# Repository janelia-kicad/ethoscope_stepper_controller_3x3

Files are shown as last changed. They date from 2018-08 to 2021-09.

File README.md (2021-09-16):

- [Repository Information](#org758a3eb)
  - [Description](#orgeb4be27)
- [Images](#org71172c4)
- [Schematic](#org945219d)
- [Gerbers](#org1d6248d)
- [Bill of Materials](#orgcc7b03c)
  - [PCB Parts](#orga3dccca)
  - [Supplemental Parts](#org7db11a9)
  - [Vendor Parts Lists](#orgad09c1d)
- [Supplemental Documentation](#org79a2346)
  - [Assembly Instructions](#org838f5a4)

# Repository Information

-   **Name:** ethoscope\_stepper\_controller\_3x3
-   **Version:** 1.2
-   **License:** Open-Source Hardware
-   **URL:** <https://github.com/janelia-kicad/ethoscope_stepper_controller_3x3>
-   **Author:** Peter Polidoro
-   **Email:** peter@polidoro.io

## Description

This device controls the 7 stepper motors on the fly ethoscope rig.

# Images

# Schematic

[./schematic/ethoscope\_stepper\_controller\_3x3.pdf](./schematic/ethoscope_stepper_controller_3x3.pdf)

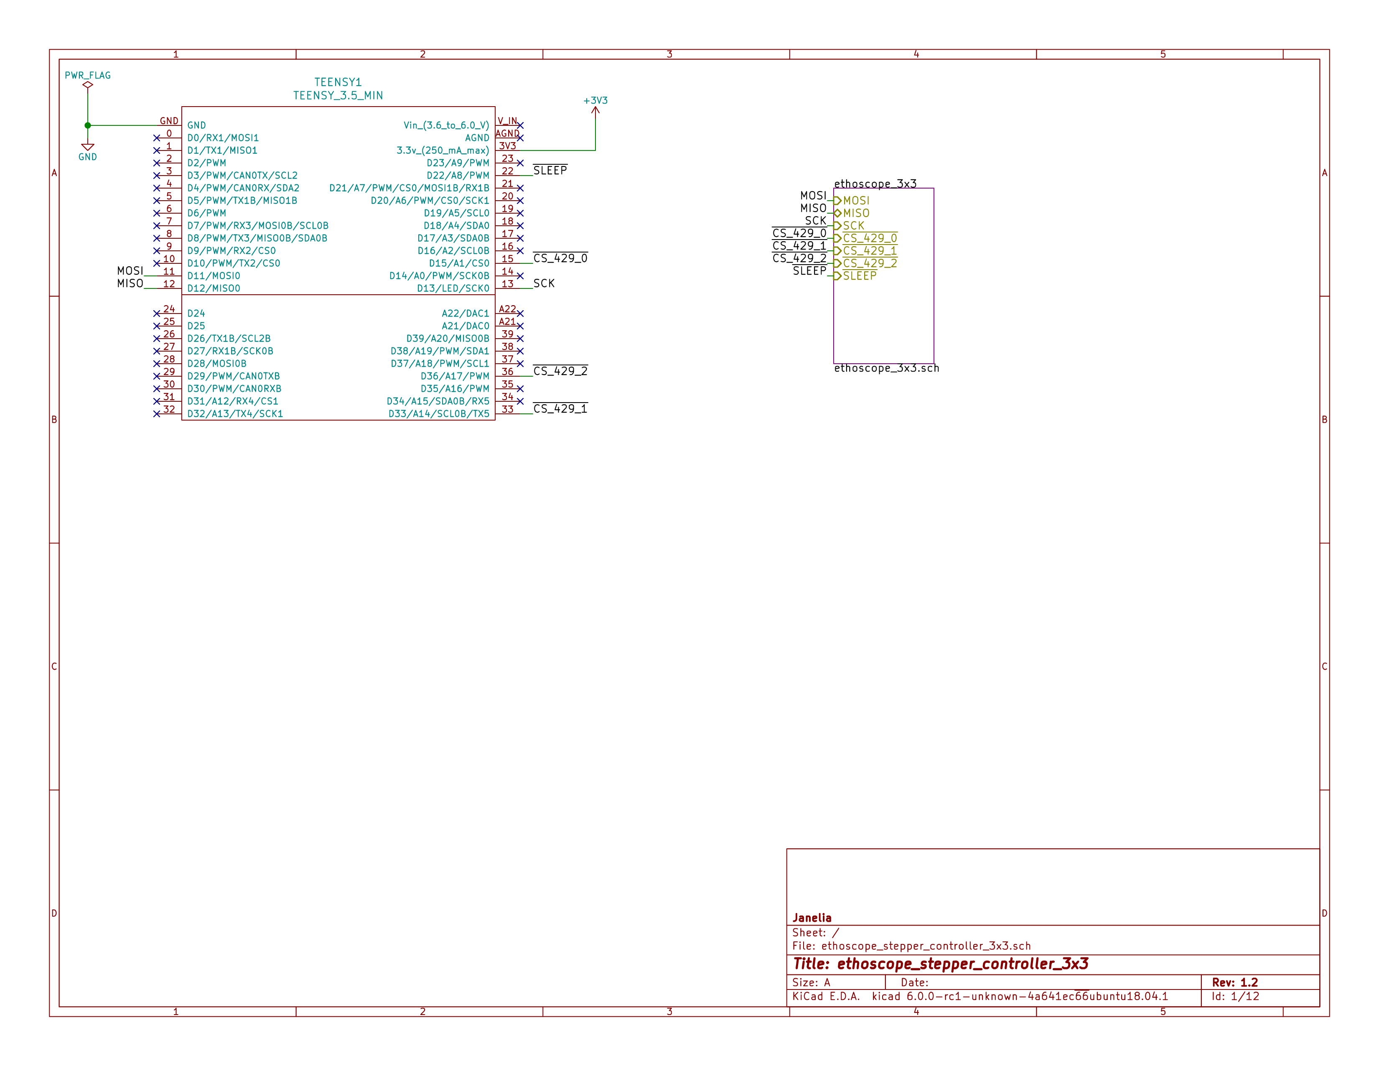
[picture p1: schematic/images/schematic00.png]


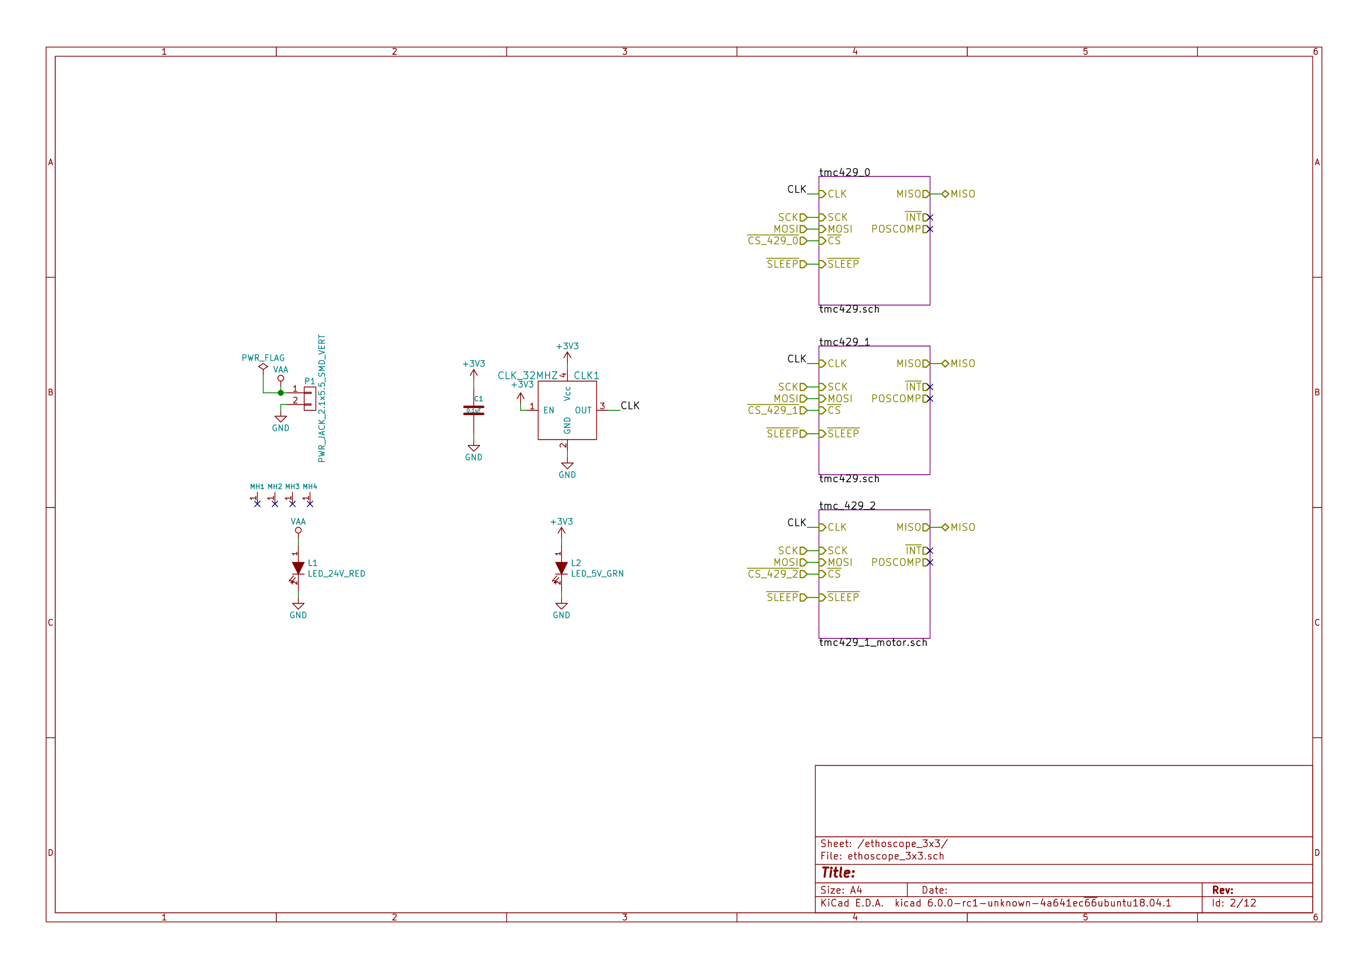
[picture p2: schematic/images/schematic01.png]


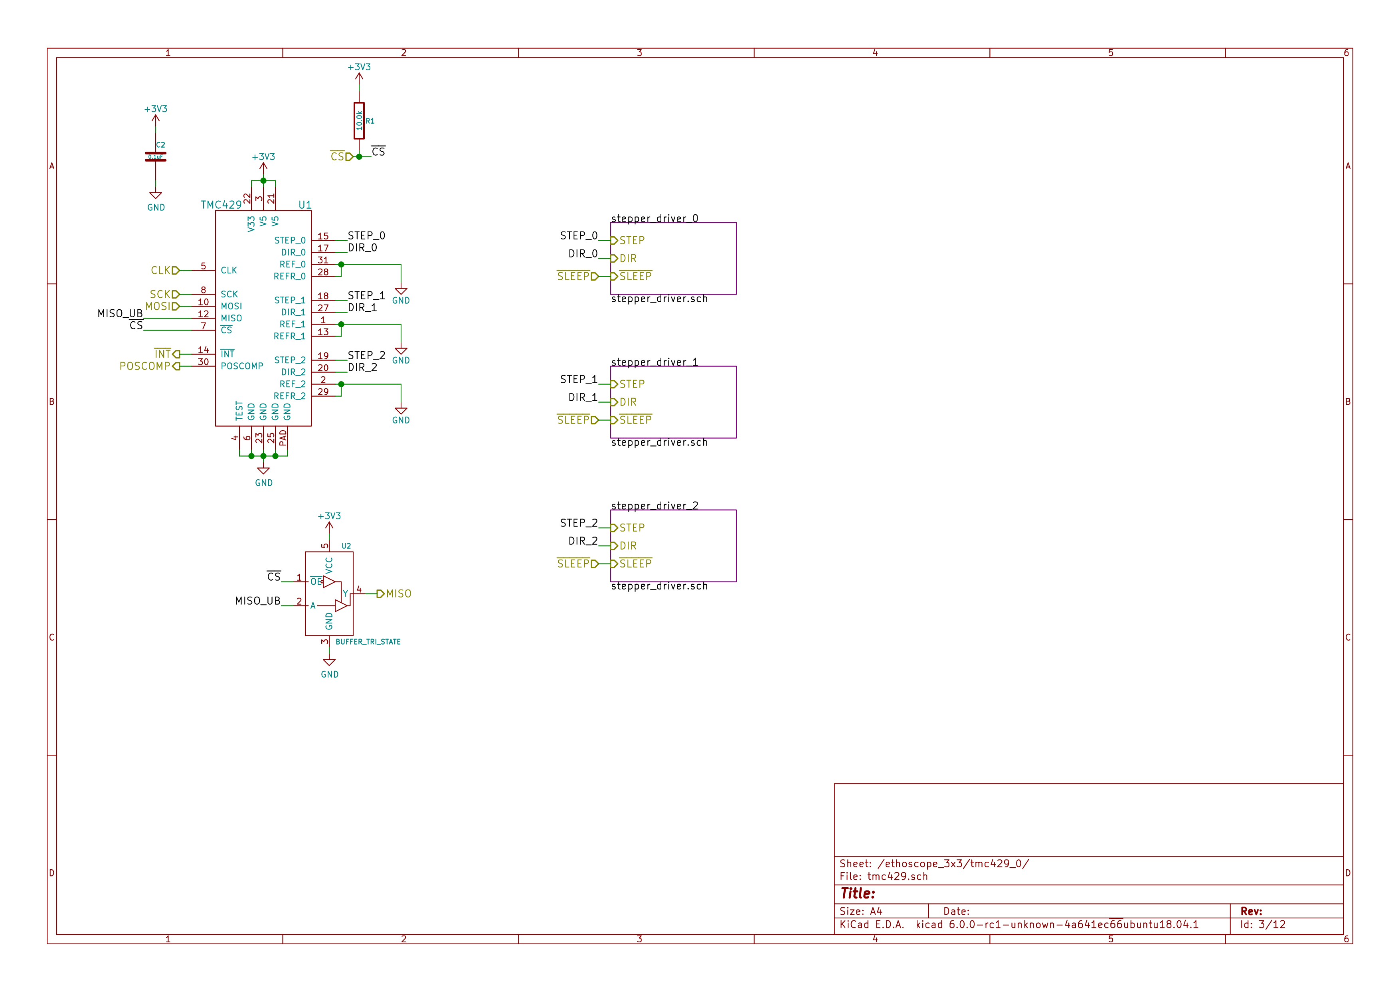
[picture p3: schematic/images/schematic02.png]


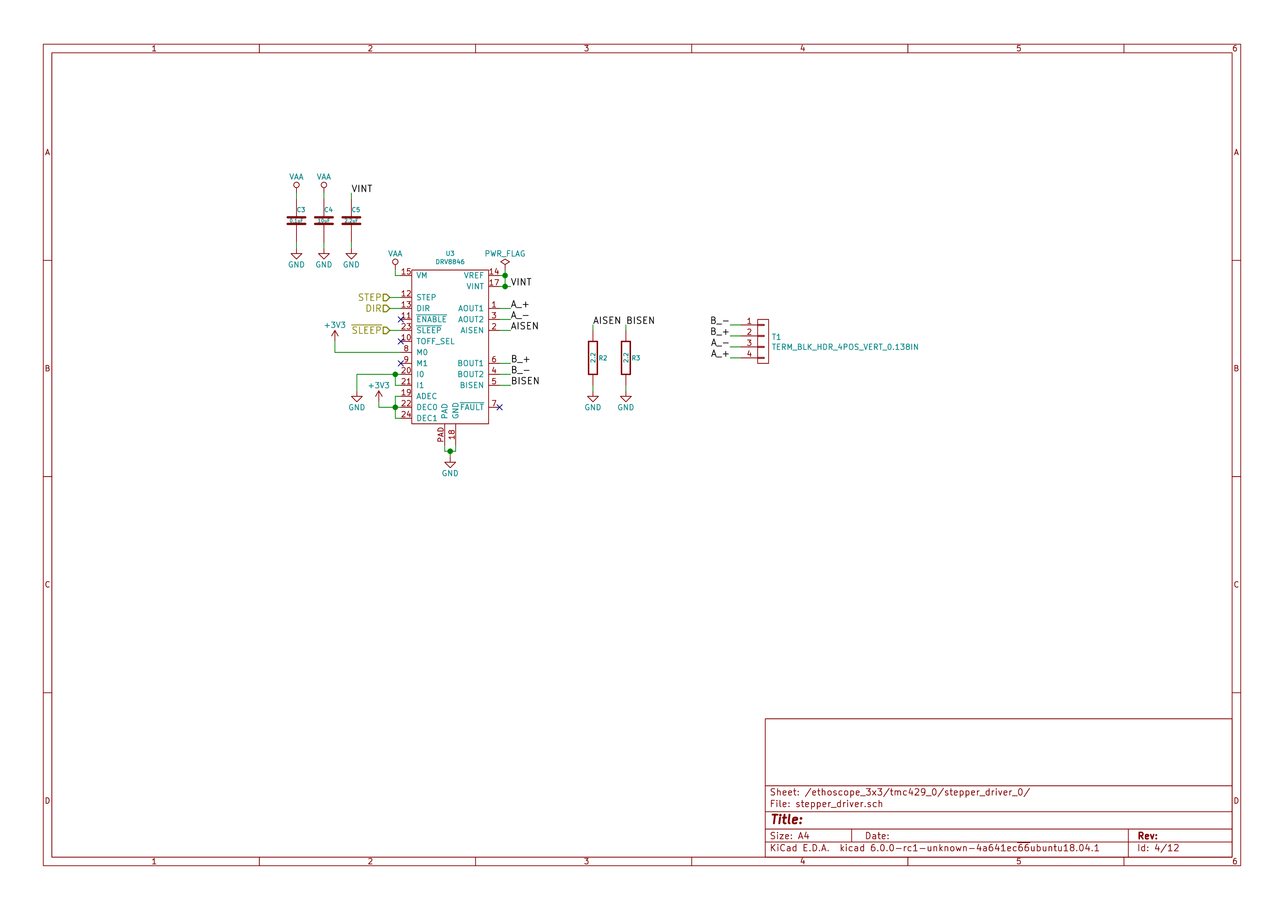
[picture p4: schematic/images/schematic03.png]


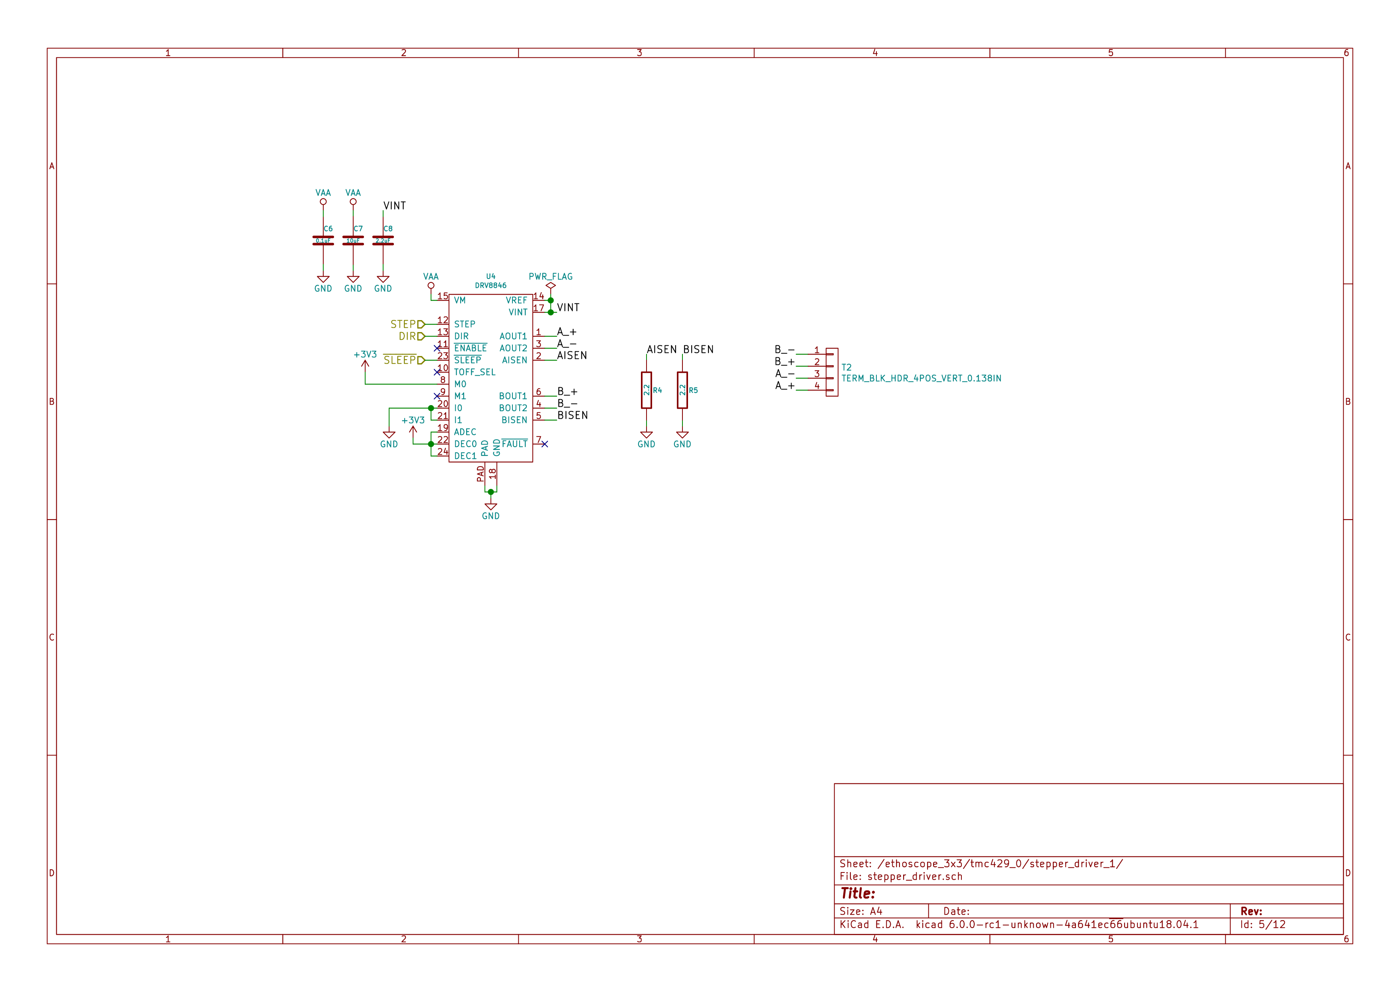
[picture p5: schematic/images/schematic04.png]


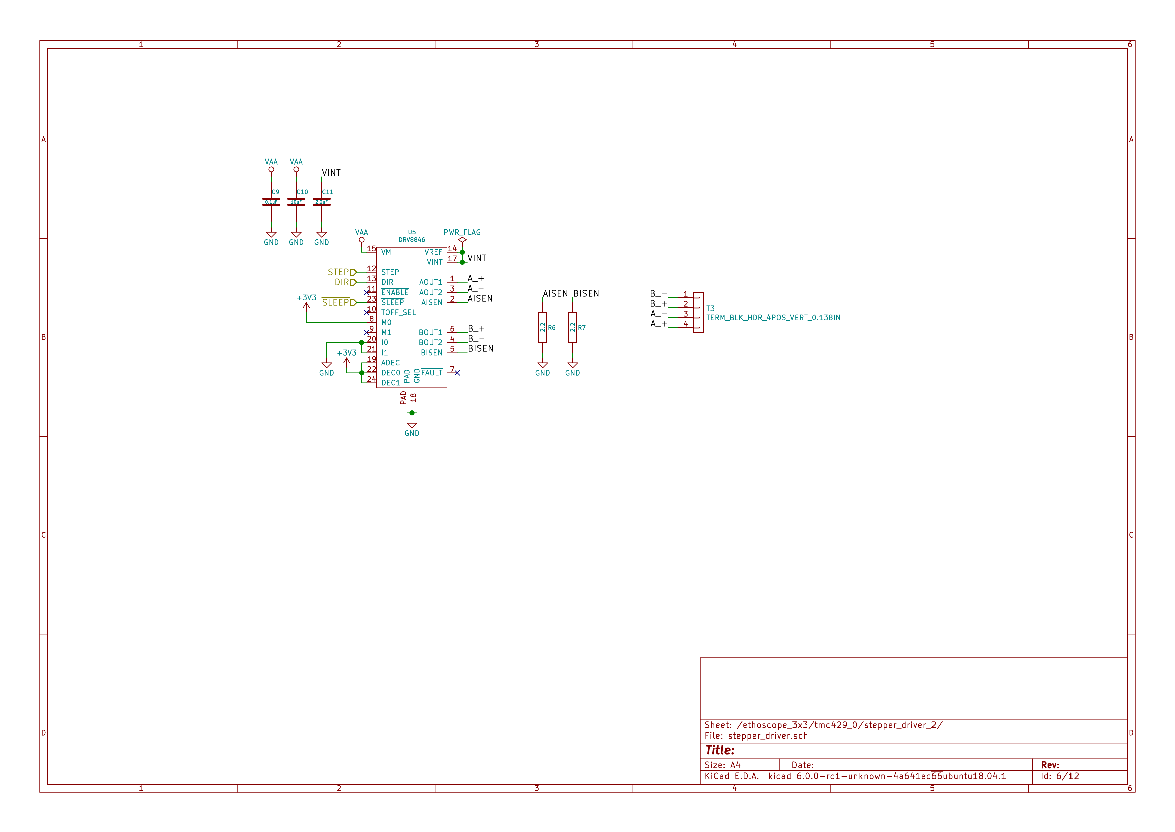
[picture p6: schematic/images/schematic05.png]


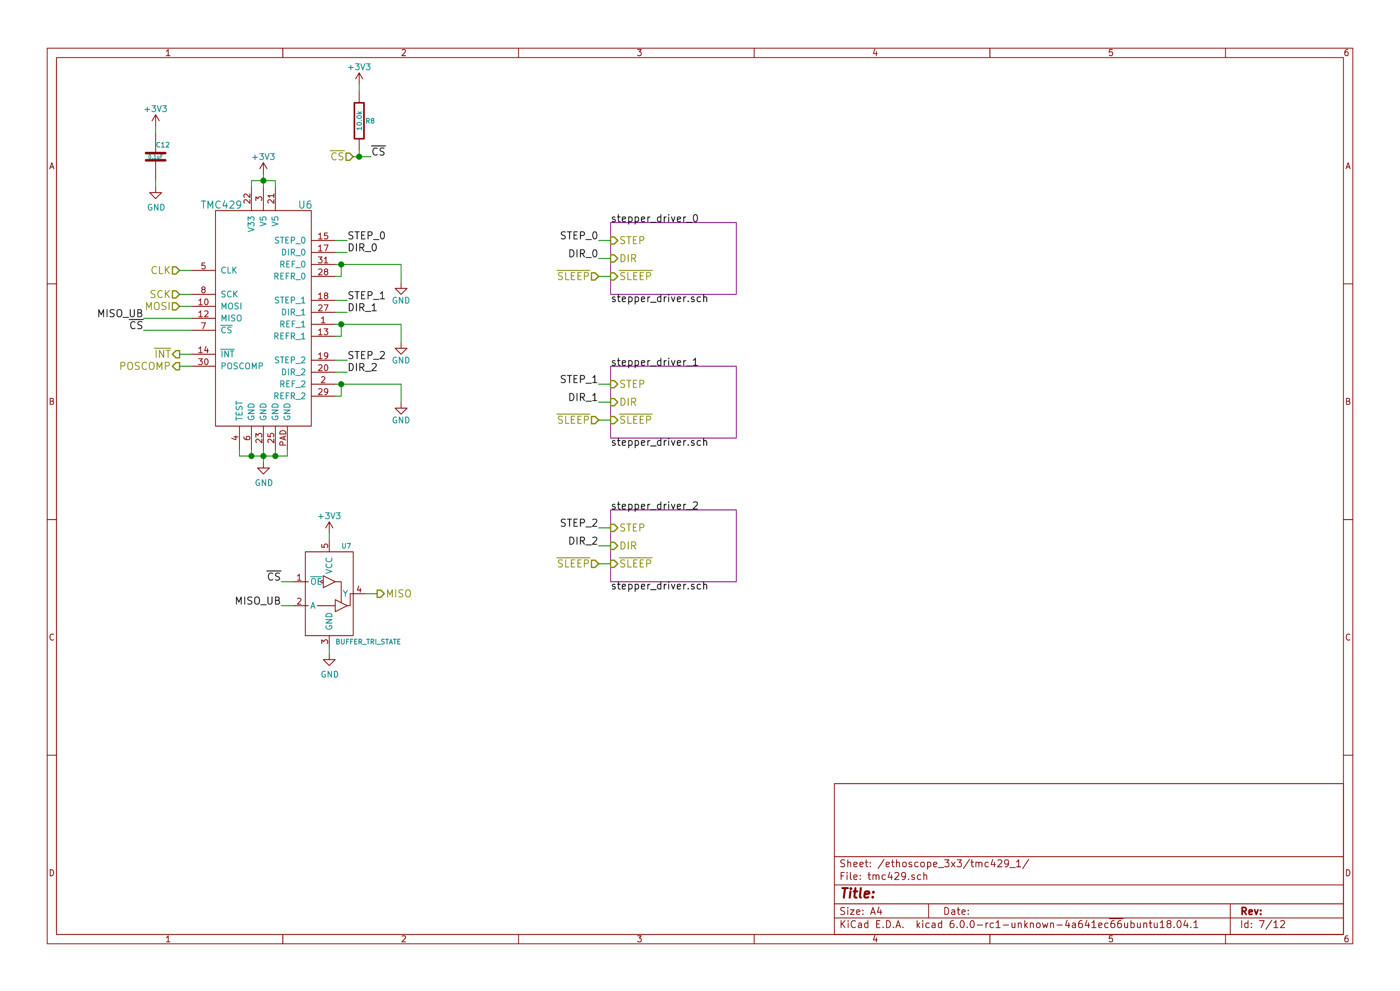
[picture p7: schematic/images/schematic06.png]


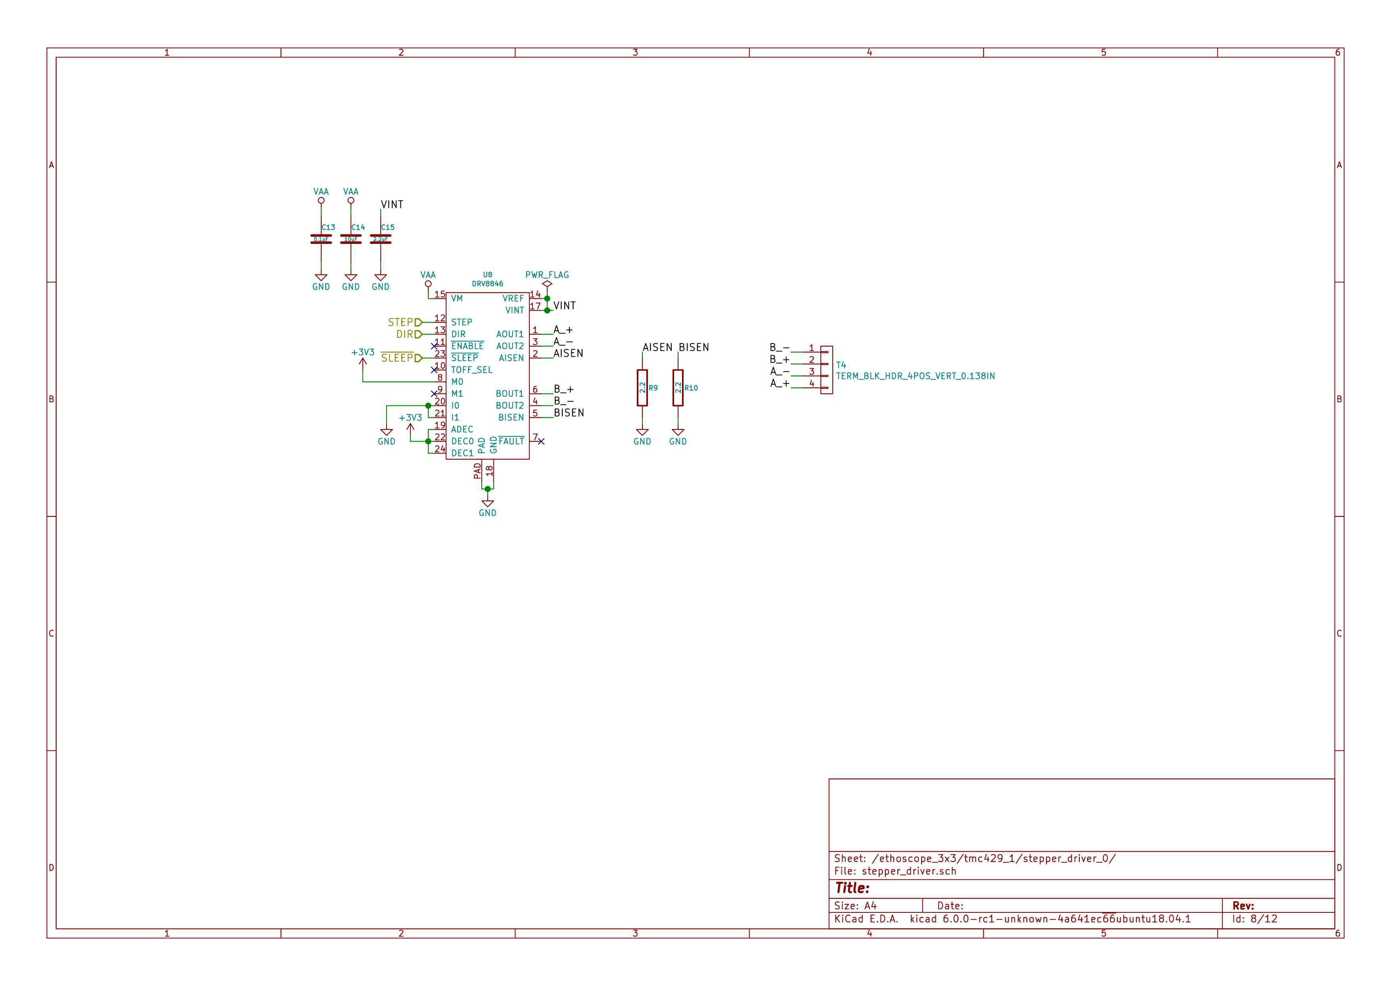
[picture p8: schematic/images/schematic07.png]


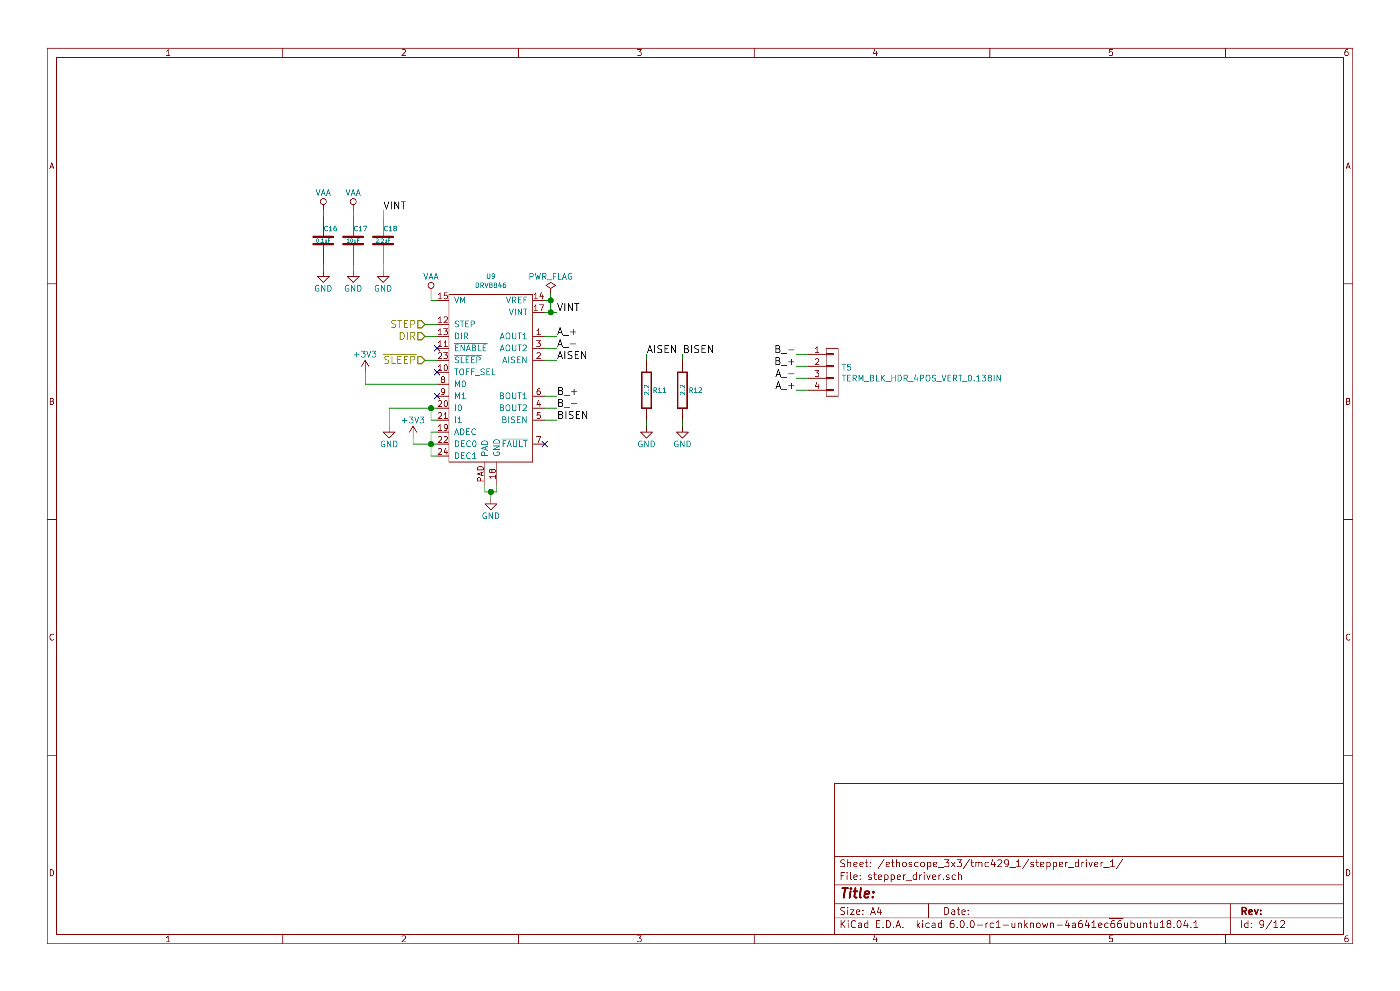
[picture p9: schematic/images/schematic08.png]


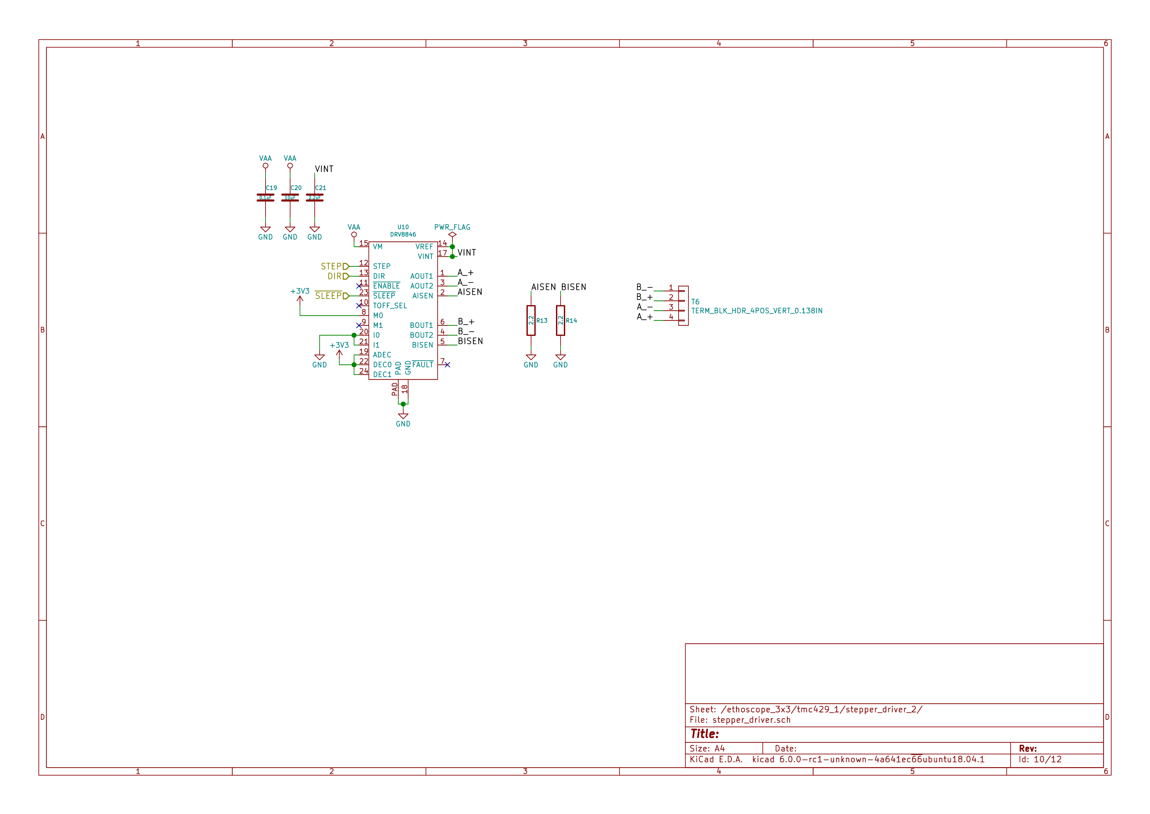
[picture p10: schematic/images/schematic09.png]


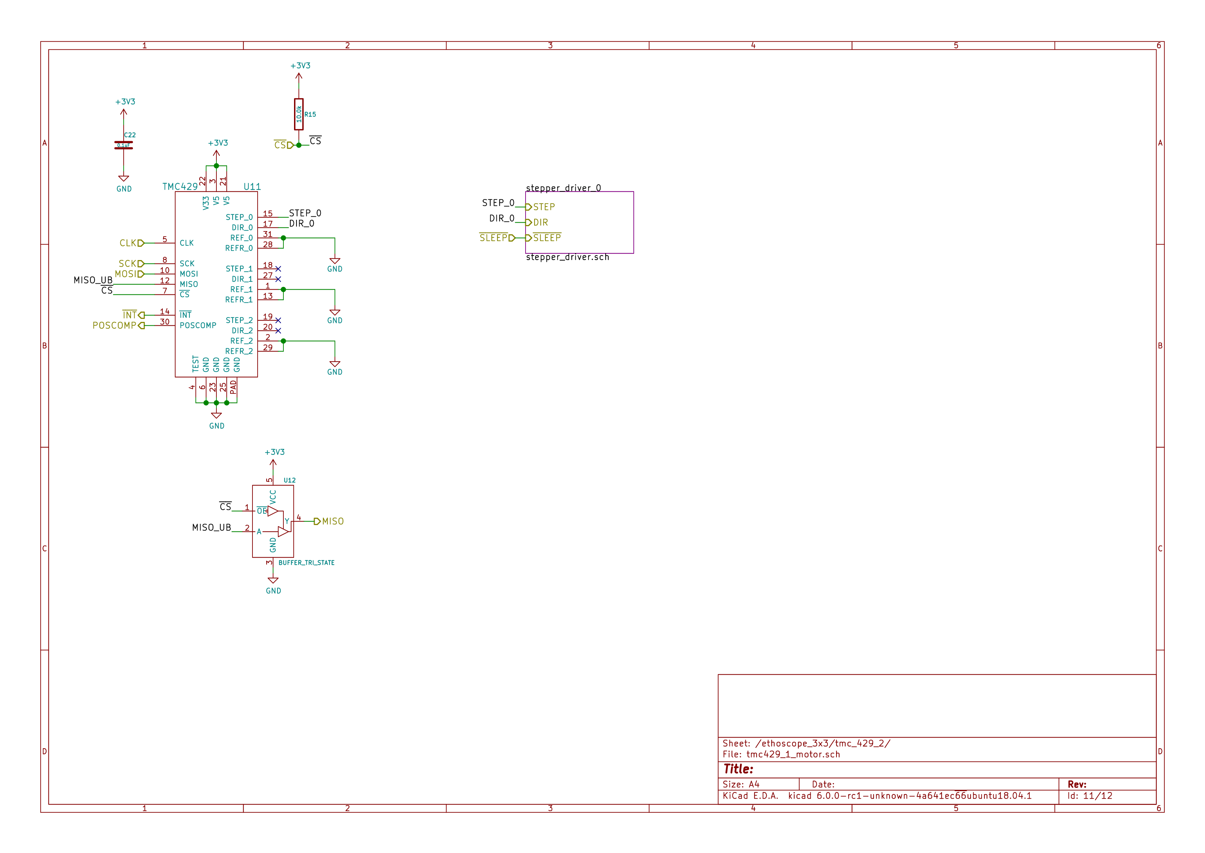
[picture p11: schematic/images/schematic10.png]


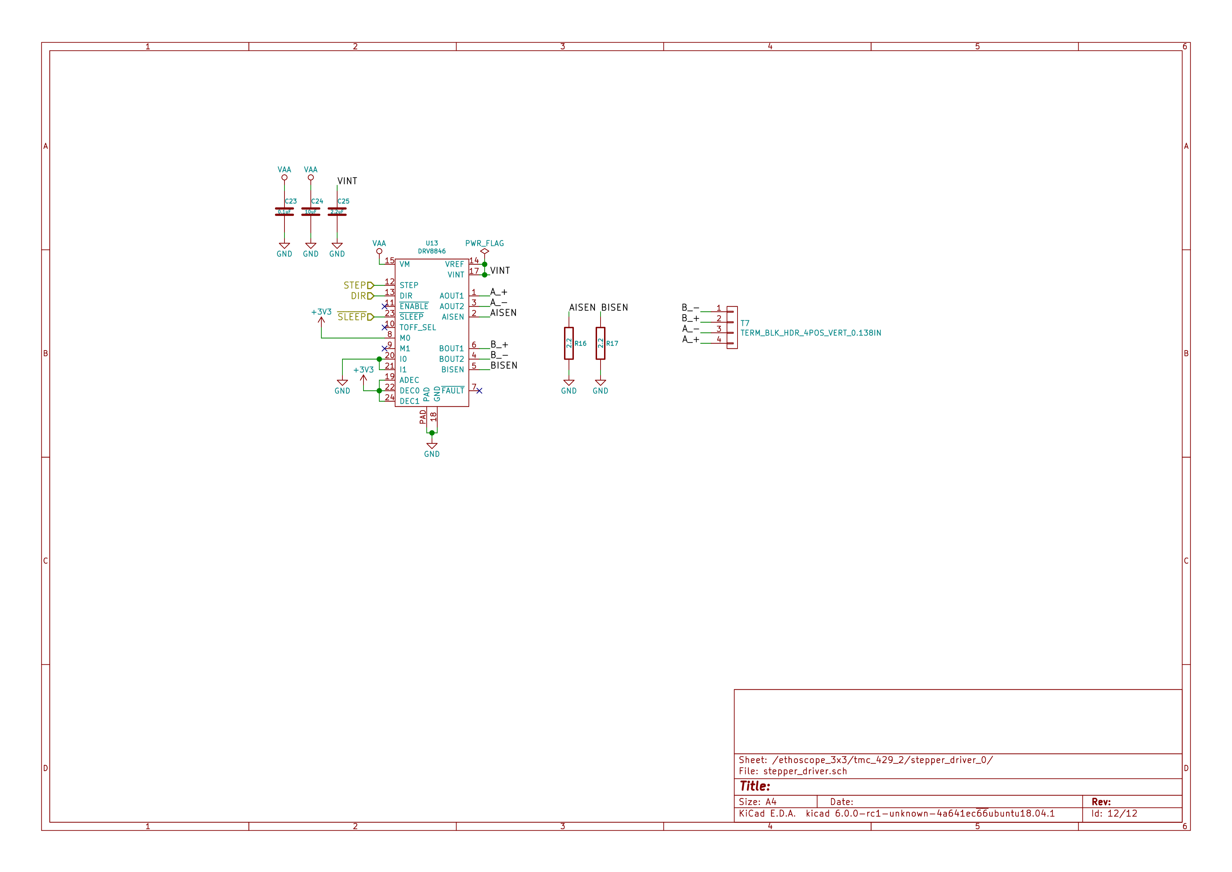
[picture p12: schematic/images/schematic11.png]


# Gerbers

Send gerbers zip file to your favorite PCB manufacturer for fabrication.

[./gerbers/ethoscope\_stepper\_controller\_3x3\_v1.2.zip](./gerbers/ethoscope_stepper_controller_3x3_v1.2.zip)

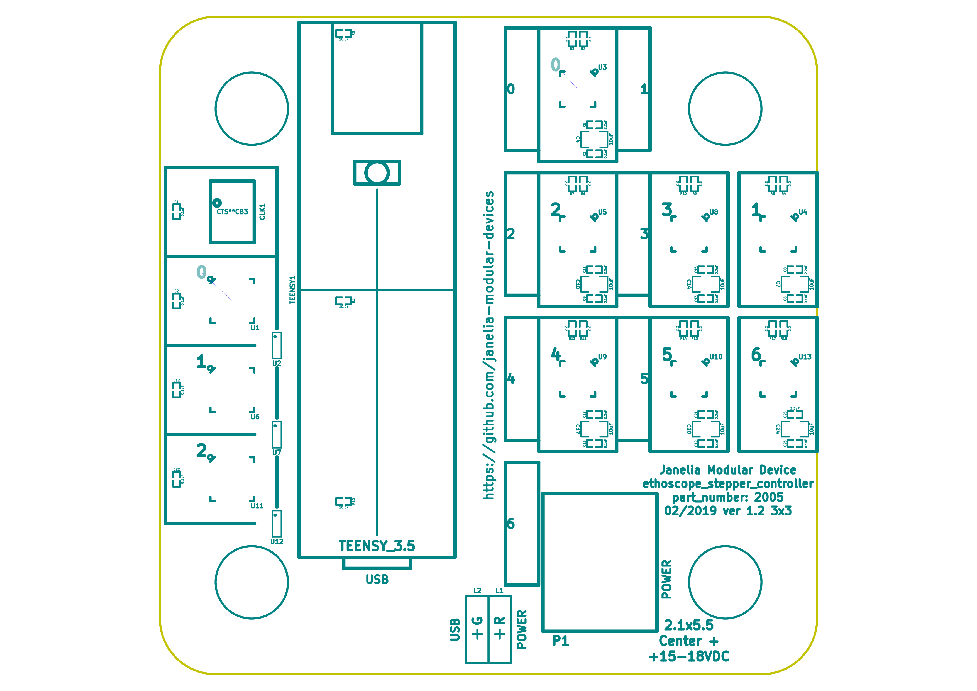
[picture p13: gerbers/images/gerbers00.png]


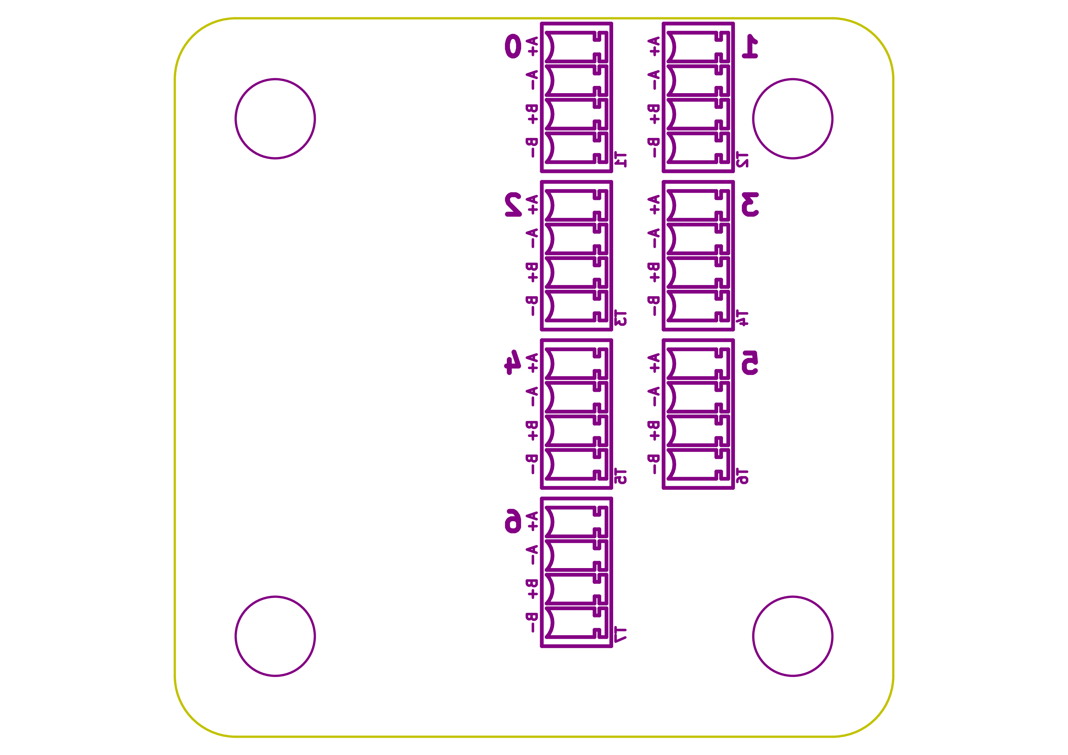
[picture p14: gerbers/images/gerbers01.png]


# Bill of Materials

## PCB Parts

| Item | Reference(s)                                     | Quantity | PartNumber       | Vendor  | Description                      |
|---- |------------------------------------------------ |-------- |---------------- |------- |-------------------------------- |
| 1    | C1 C12 C13 C16 C19 C2 C22 C23 C3 C6 C9           | 11       | 1276-1739-1-ND   | digikey | CAP CER 0.1UF 25V Y5V 0402       |
| 2    | C10 C14 C17 C20 C24 C4 C7                        | 7        | 445-14419-1-ND   | digikey | CAP CER 10UF 35V X5R 0805        |
| 3    | C11 C15 C18 C21 C25 C5 C8                        | 7        | 445-9028-1-ND    | digikey | CAP CER 2.2UF 35V X5R 0402       |
| 4    | CLK1                                             | 1        | CTX277LVCT-ND    | digikey | OSC XO 32.000MHZ HCMOS TTL SMD   |
| 5    | L1                                               | 1        | 350-1723-ND      | digikey | LED 2MM 24V VERTICAL RED PC MNT  |
| 6    | L2                                               | 1        | 350-1726-ND      | digikey | LED 2MM 5V VERTICAL GREEN PC MNT |
| 7    | MH1 MH2 MH3 MH4                                  | 4        | 36-2441-ND       | digikey | SHLDR SCREW RND HEAD HEX 4-40    |
| 8    | P1                                               | 1        | CP-015AHPJ-CT-ND | digikey | CONN PWR JACK 2X5.5MM SOLDER     |
| 9    | R1 R15 R8                                        | 3        | P10KJCT-ND       | digikey | RES SMD 10K OHM 5% 1/10W 0402    |
| 10   | R10 R11 R12 R13 R14 R16 R17 R2 R3 R4 R5 R6 R7 R9 | 14       | RL05S2.2FCT-ND   | digikey | RES SMD 2.2 OHM 1% 1/6W 0402     |
| 11   | T1 T2 T3 T4 T5 T6 T7                             | 7        | 277-5738-ND      | digikey | TERM BLOCK HDR 4POS VERT 3.5MM   |
| 12   | TEENSY1                                          | 1        | 1568-1464-ND     | digikey | TEENSY 3.5 (HEADERS)             |
| 13   | U1 U11 U6                                        | 3        | 1460-1071-1-ND   | digikey | IC MOTOR CONTROLLER SPI 32QFN    |
| 14   | U10 U13 U3 U4 U5 U8 U9                           | 7        | 296-40083-1-ND   | digikey | IC MOTOR DRIVER PAR 24VQFN       |
| 15   | U12 U2 U7                                        | 3        | 296-11603-1-ND   | digikey | IC BUF NON-INVERT 5.5V SOT23-5   |

## Supplemental Parts

| Item | Quantity | PartNumber   | Vendor  | Description                      |
|---- |-------- |------------ |------- |-------------------------------- |
| 1    | 1        | 102-4531-ND  | digikey | AC-DC 18 VDC 2 A SW C14 DESK     |
| 2    | 1        | 1175-1298-ND | digikey | CORD PWR MALE-FEMALE STR 2M      |
| 3    | 1        | 1175-1694-ND | digikey | CABLE USB-A TO MICRO USB-B .5M   |
| 4    | 2        | 1212-1209-ND | digikey | SOCKET 7 MM SOLDER TAIL SINGLE   |
| 5    | 28       | 277-2433-ND  | digikey | FERRULES WITH PLASTIC SLEEVE YEL |
| 6    | 7        | 277-2418-ND  | digikey | TERM BLOCK PLUG 4POS STR 3.5MM   |
| 7    | 7        | P14333-ND    | digikey | STEP MOTOR PM GEARED BIPOLAR 15V |

## Vendor Parts Lists

[./bom/digikey\_parts.csv](./bom/digikey_parts.csv)

[./bom/supplemental\_digikey\_parts.csv](./bom/supplemental_digikey_parts.csv)

# Supplemental Documentation

## Assembly Instructions

-   Solder surface mount and through hole components onto the pcb.

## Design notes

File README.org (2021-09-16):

# Created 2019-02-06 Wed 09:52
#+OPTIONS: title:nil author:nil email:nil toc:t |:t ^:nil
* Repository Information

- Name :: ethoscope_stepper_controller_3x3
- Version :: 1.2
- License :: Open-Source Hardware
- URL :: https://github.com/janelia-kicad/ethoscope_stepper_controller_3x3
- Author :: Peter Polidoro
- Email :: peter@polidoro.io

** Description

This device controls the 7 stepper motors on the fly ethoscope rig.

* Images

* Schematic

[[file:./schematic/ethoscope_stepper_controller_3x3.pdf][./schematic/ethoscope_stepper_controller_3x3.pdf]]

























* Gerbers

Send gerbers zip file to your favorite PCB manufacturer for fabrication.

[[file:./gerbers/ethoscope_stepper_controller_3x3_v1.2.zip][./gerbers/ethoscope_stepper_controller_3x3_v1.2.zip]]





* Bill of Materials

** PCB Parts

| Item | Reference(s)                                     | Quantity | PartNumber       | Vendor  | Description                      |
|------+--------------------------------------------------+----------+------------------+---------+----------------------------------|
|    1 | C1 C12 C13 C16 C19 C2 C22 C23 C3 C6 C9           |       11 | 1276-1739-1-ND   | digikey | CAP CER 0.1UF 25V Y5V 0402       |
|    2 | C10 C14 C17 C20 C24 C4 C7                        |        7 | 445-14419-1-ND   | digikey | CAP CER 10UF 35V X5R 0805        |
|    3 | C11 C15 C18 C21 C25 C5 C8                        |        7 | 445-9028-1-ND    | digikey | CAP CER 2.2UF 35V X5R 0402       |
|    4 | CLK1                                             |        1 | CTX277LVCT-ND    | digikey | OSC XO 32.000MHZ HCMOS TTL SMD   |
|    5 | L1                                               |        1 | 350-1723-ND      | digikey | LED 2MM 24V VERTICAL RED PC MNT  |
|    6 | L2                                               |        1 | 350-1726-ND      | digikey | LED 2MM 5V VERTICAL GREEN PC MNT |
|    7 | MH1 MH2 MH3 MH4                                  |        4 | 36-2441-ND       | digikey | SHLDR SCREW RND HEAD HEX 4-40    |
|    8 | P1                                               |        1 | CP-015AHPJ-CT-ND | digikey | CONN PWR JACK 2X5.5MM SOLDER     |
|    9 | R1 R15 R8                                        |        3 | P10KJCT-ND       | digikey | RES SMD 10K OHM 5% 1/10W 0402    |
|   10 | R10 R11 R12 R13 R14 R16 R17 R2 R3 R4 R5 R6 R7 R9 |       14 | RL05S2.2FCT-ND   | digikey | RES SMD 2.2 OHM 1% 1/6W 0402     |
|   11 | T1 T2 T3 T4 T5 T6 T7                             |        7 | 277-5738-ND      | digikey | TERM BLOCK HDR 4POS VERT 3.5MM   |
|   12 | TEENSY1                                          |        1 | 1568-1464-ND     | digikey | TEENSY 3.5 (HEADERS)             |
|   13 | U1 U11 U6                                        |        3 | 1460-1071-1-ND   | digikey | IC MOTOR CONTROLLER SPI 32QFN    |
|   14 | U10 U13 U3 U4 U5 U8 U9                           |        7 | 296-40083-1-ND   | digikey | IC MOTOR DRIVER PAR 24VQFN       |
|   15 | U12 U2 U7                                        |        3 | 296-11603-1-ND   | digikey | IC BUF NON-INVERT 5.5V SOT23-5   |

** Supplemental Parts

| Item | Quantity | PartNumber   | Vendor  | Description                      |
|------+----------+--------------+---------+----------------------------------|
|    1 |        1 | 102-4531-ND  | digikey | AC-DC 18 VDC 2 A SW C14 DESK     |
|    2 |        1 | 1175-1298-ND | digikey | CORD PWR MALE-FEMALE STR 2M      |
|    3 |        1 | 1175-1694-ND | digikey | CABLE USB-A TO MICRO USB-B .5M   |
|    4 |        2 | 1212-1209-ND | digikey | SOCKET 7 MM SOLDER TAIL SINGLE   |
|    5 |       28 | 277-2433-ND  | digikey | FERRULES WITH PLASTIC SLEEVE YEL |
|    6 |        7 | 277-2418-ND  | digikey | TERM BLOCK PLUG 4POS STR 3.5MM   |
|    7 |        7 | P14333-ND    | digikey | STEP MOTOR PM GEARED BIPOLAR 15V |

** Vendor Parts Lists

[[file:./bom/digikey_parts.csv][./bom/digikey_parts.csv]]

[[file:./bom/supplemental_digikey_parts.csv][./bom/supplemental_digikey_parts.csv]]

* Supplemental Documentation

** Assembly Instructions

- Solder surface mount and through hole components onto the pcb.

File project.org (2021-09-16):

* Header                                                           :noexport:

  #+MACRO: name ethoscope_stepper_controller_3x3
  #+MACRO: version 1.2
  #+MACRO: license Open-Source Hardware
  #+MACRO: url https://github.com/janelia-kicad/ethoscope_stepper_controller_3x3
  #+AUTHOR: Peter Polidoro
  #+EMAIL: peter@polidoro.io

* Description

  This device controls the 7 stepper motors on the fly ethoscope rig.

* Assembly Instructions

  - Solder surface mount and through hole components onto the pcb.

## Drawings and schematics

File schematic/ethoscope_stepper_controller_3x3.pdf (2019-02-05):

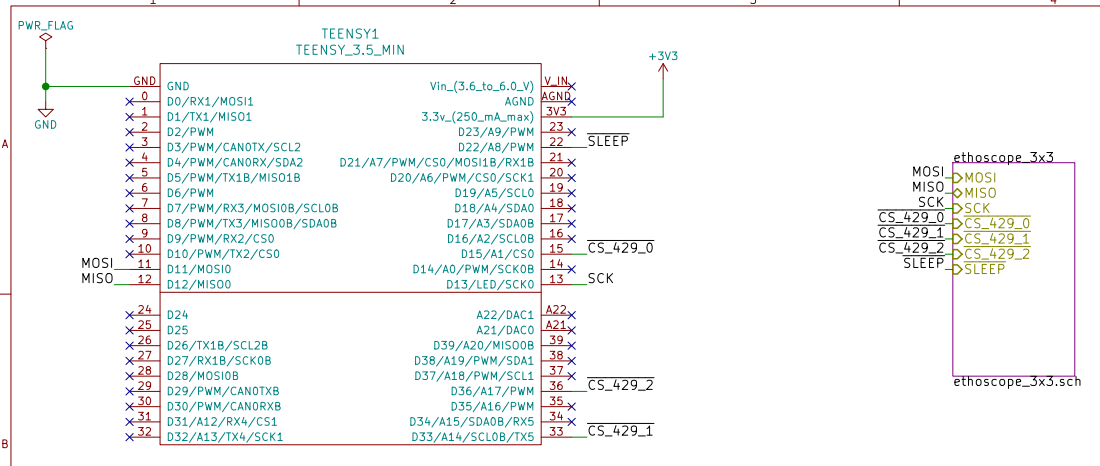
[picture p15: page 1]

File: ethoscope_stepper_controller_3x3.sch Sheet: / Janelia

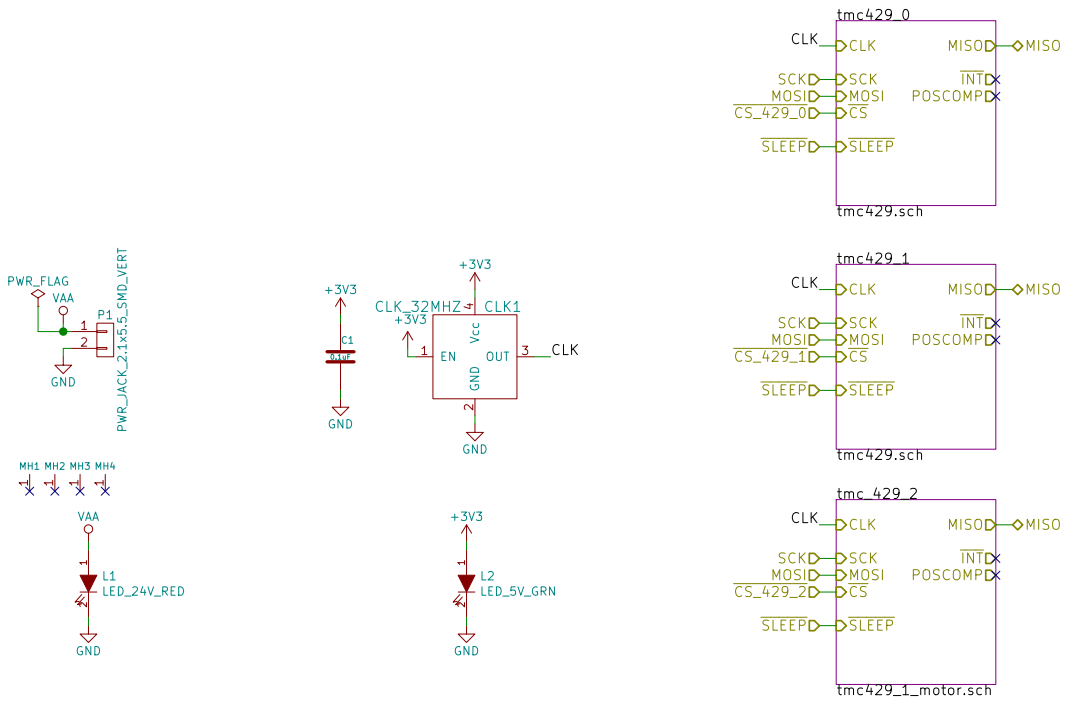
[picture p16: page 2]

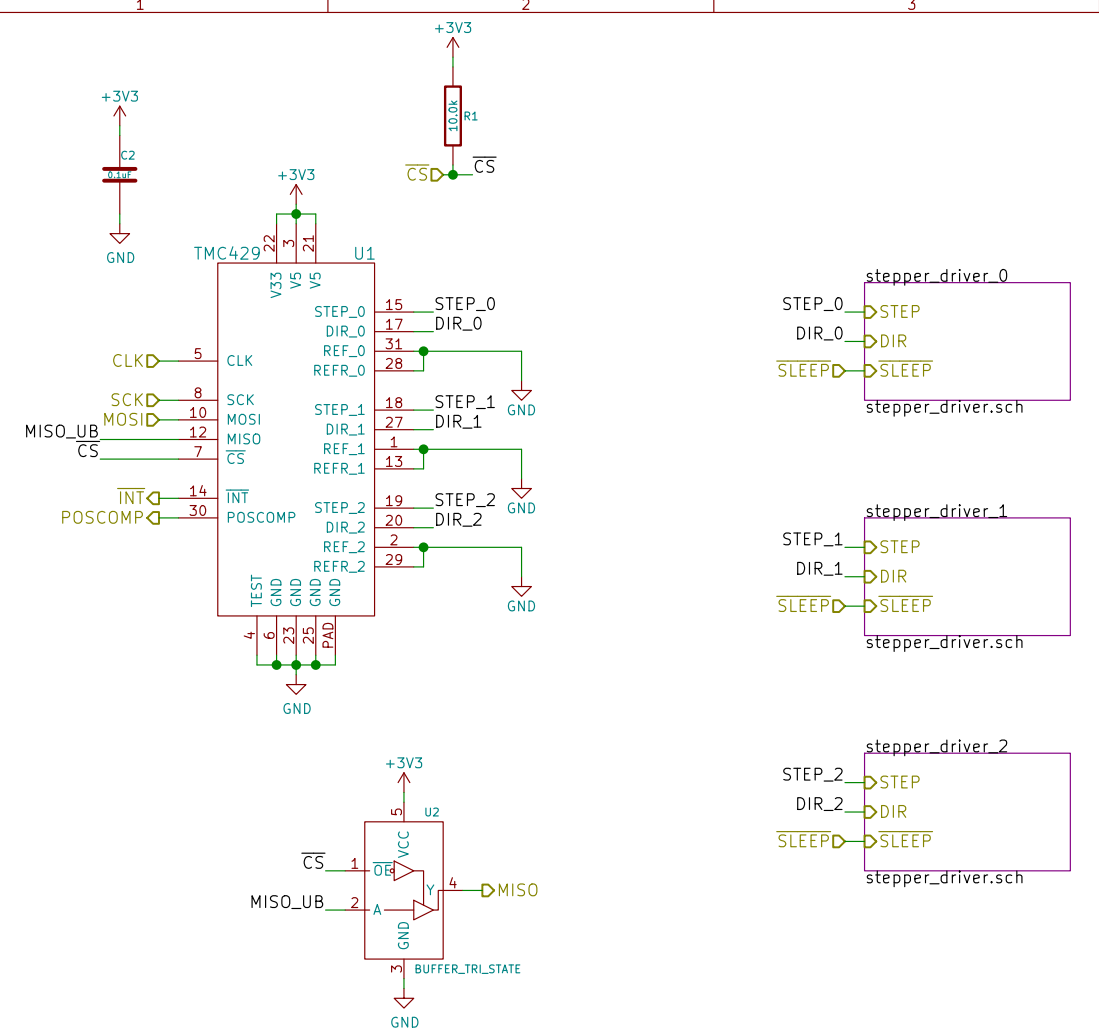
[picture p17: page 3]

6 CS 7 SCK 8 GND PAD

Id: 3/12 Title: File: tmc429.sch Sheet: /ethoscope_3x3/tmc429_0/

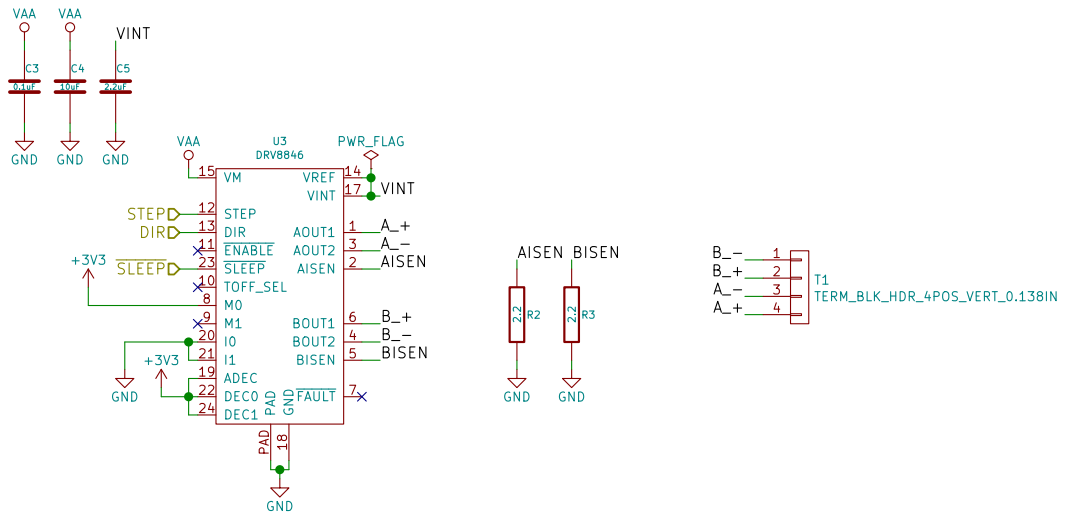
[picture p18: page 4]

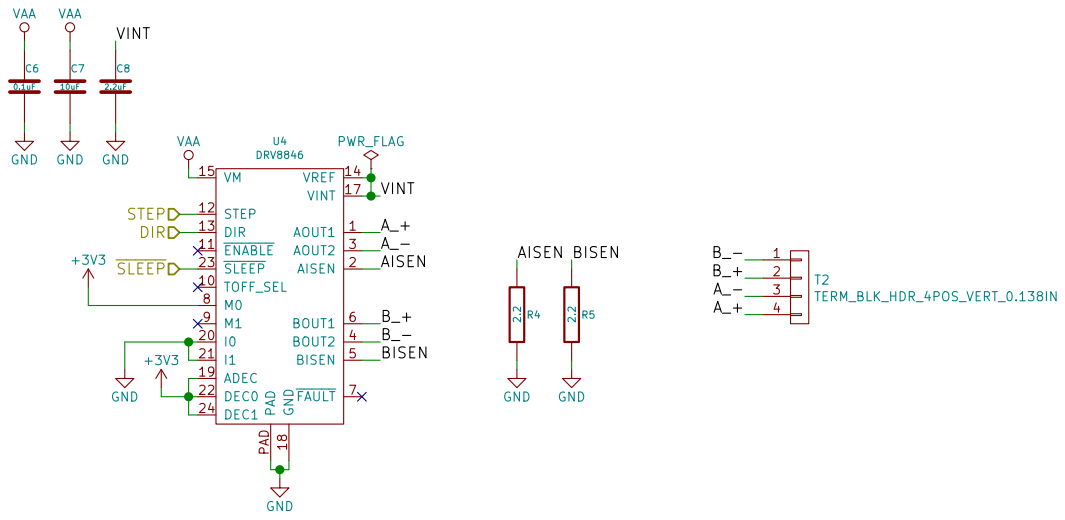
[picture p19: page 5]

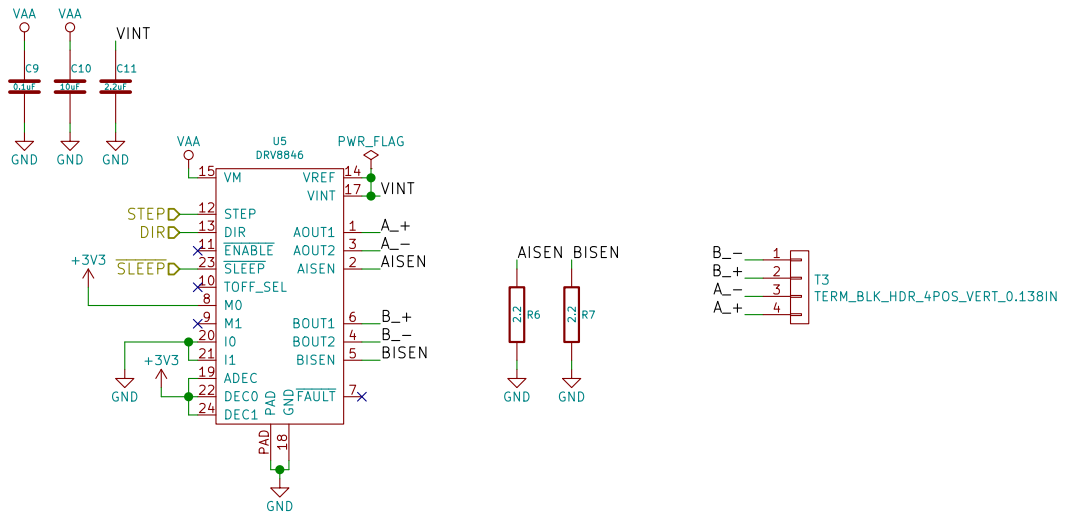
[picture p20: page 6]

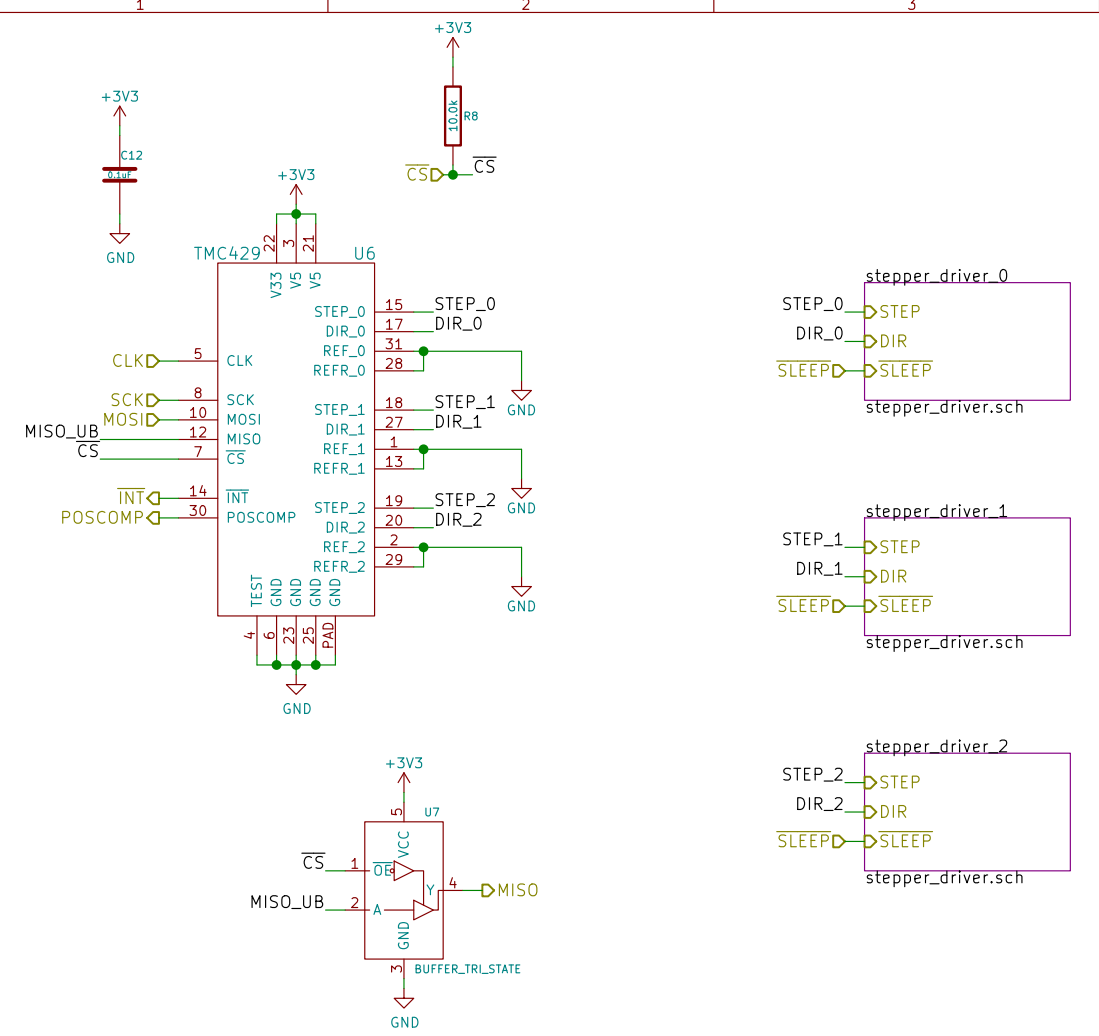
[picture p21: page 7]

6 CS 7 SCK 8 GND PAD

Id: 7/12 Title: File: tmc429.sch Sheet: /ethoscope_3x3/tmc429_1/

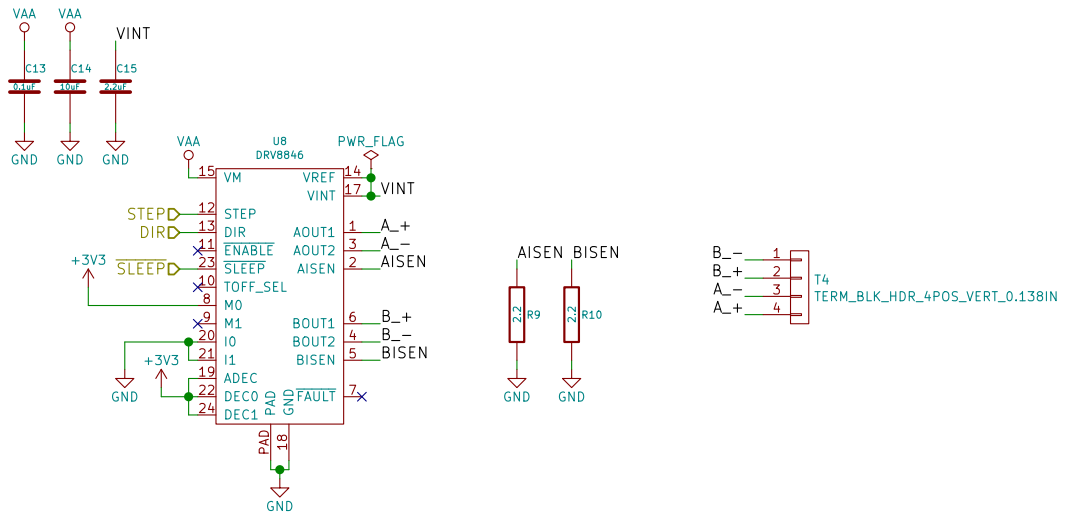
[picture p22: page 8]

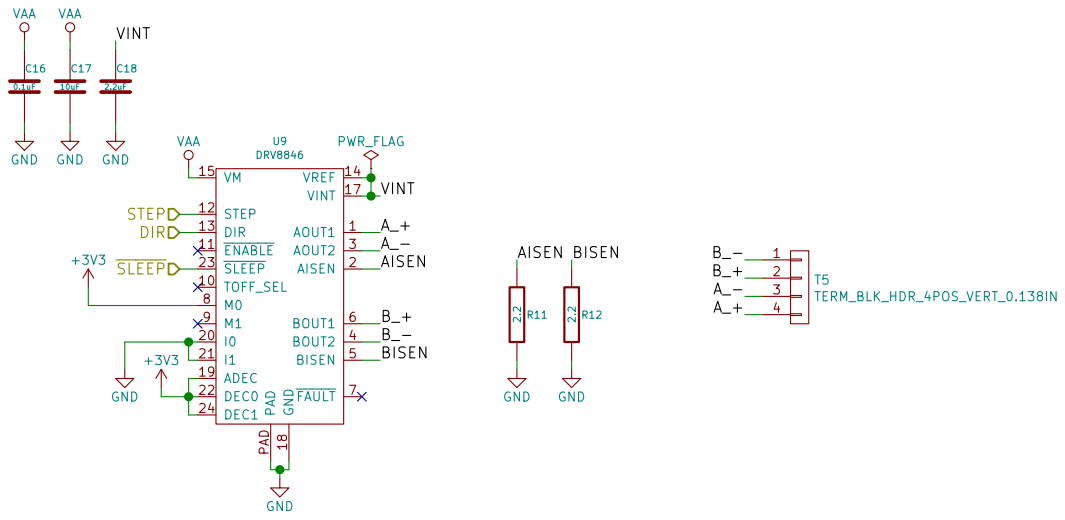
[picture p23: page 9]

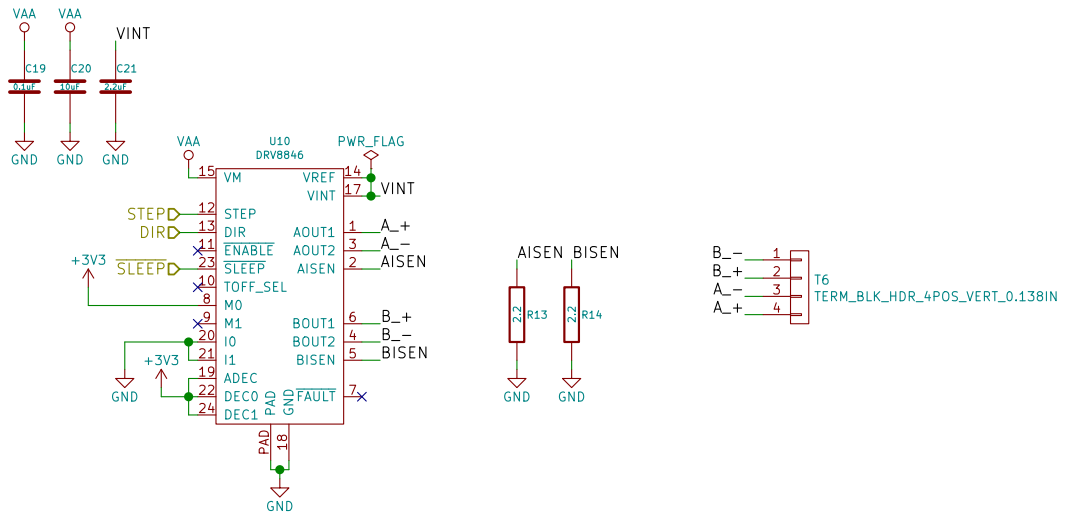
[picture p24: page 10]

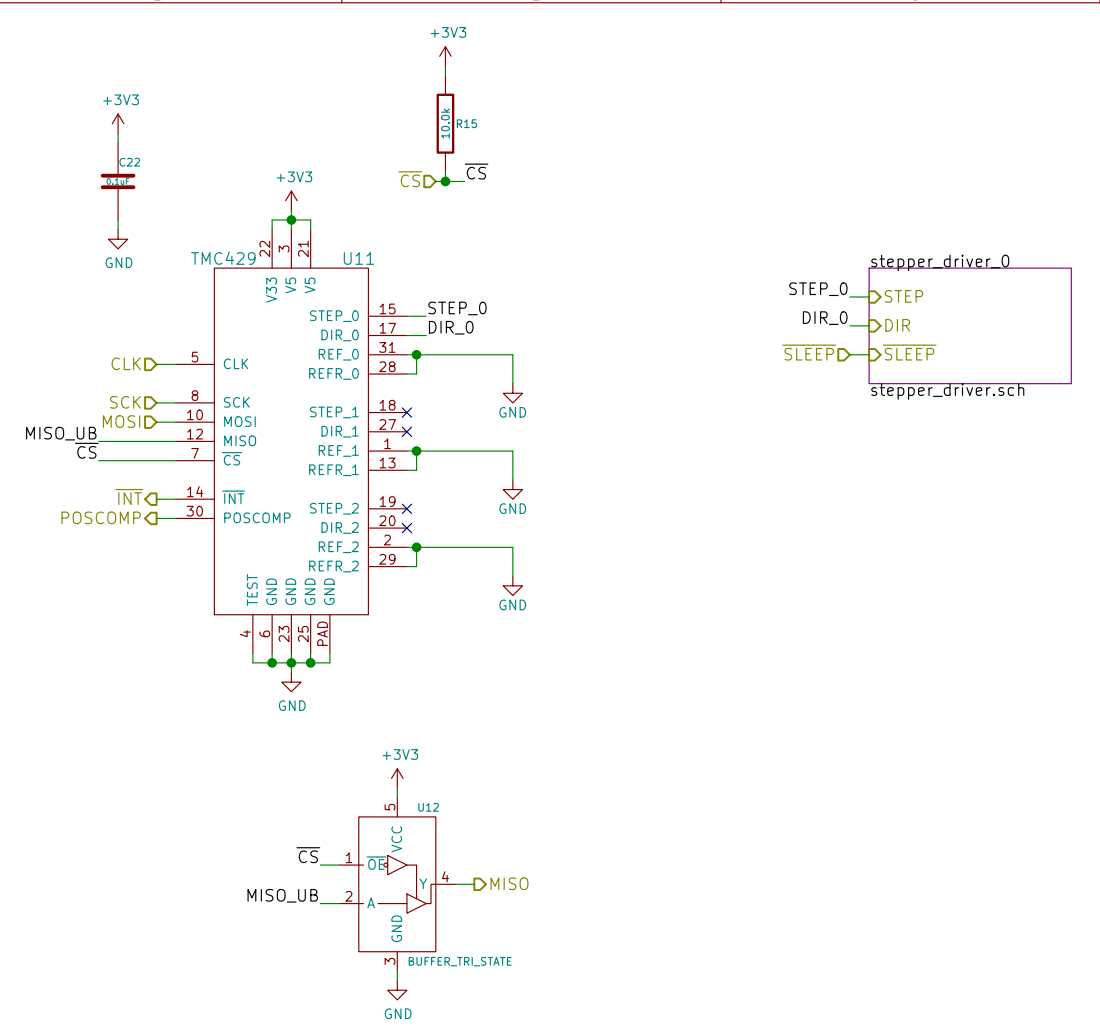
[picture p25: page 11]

6 CS 7 SCK 8 GND PAD

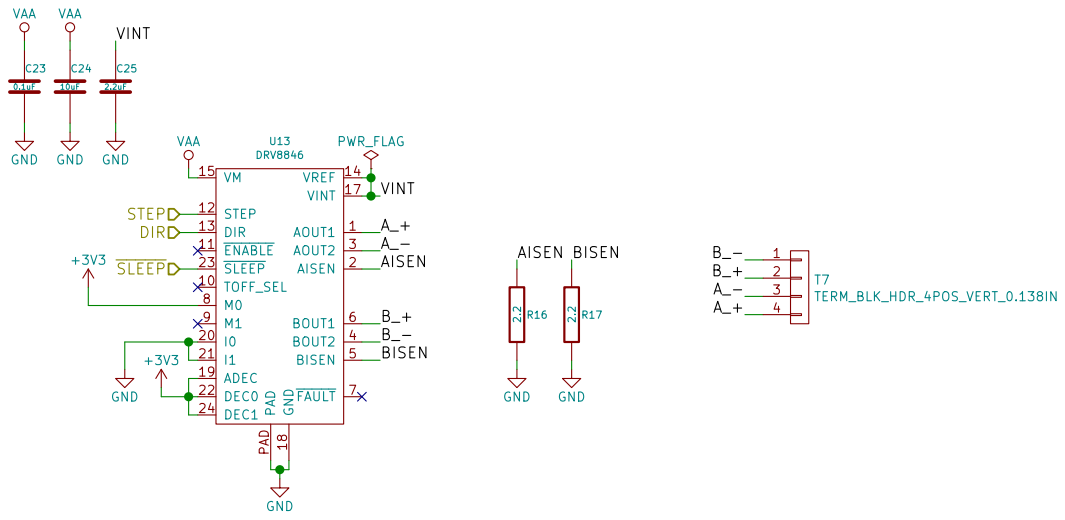
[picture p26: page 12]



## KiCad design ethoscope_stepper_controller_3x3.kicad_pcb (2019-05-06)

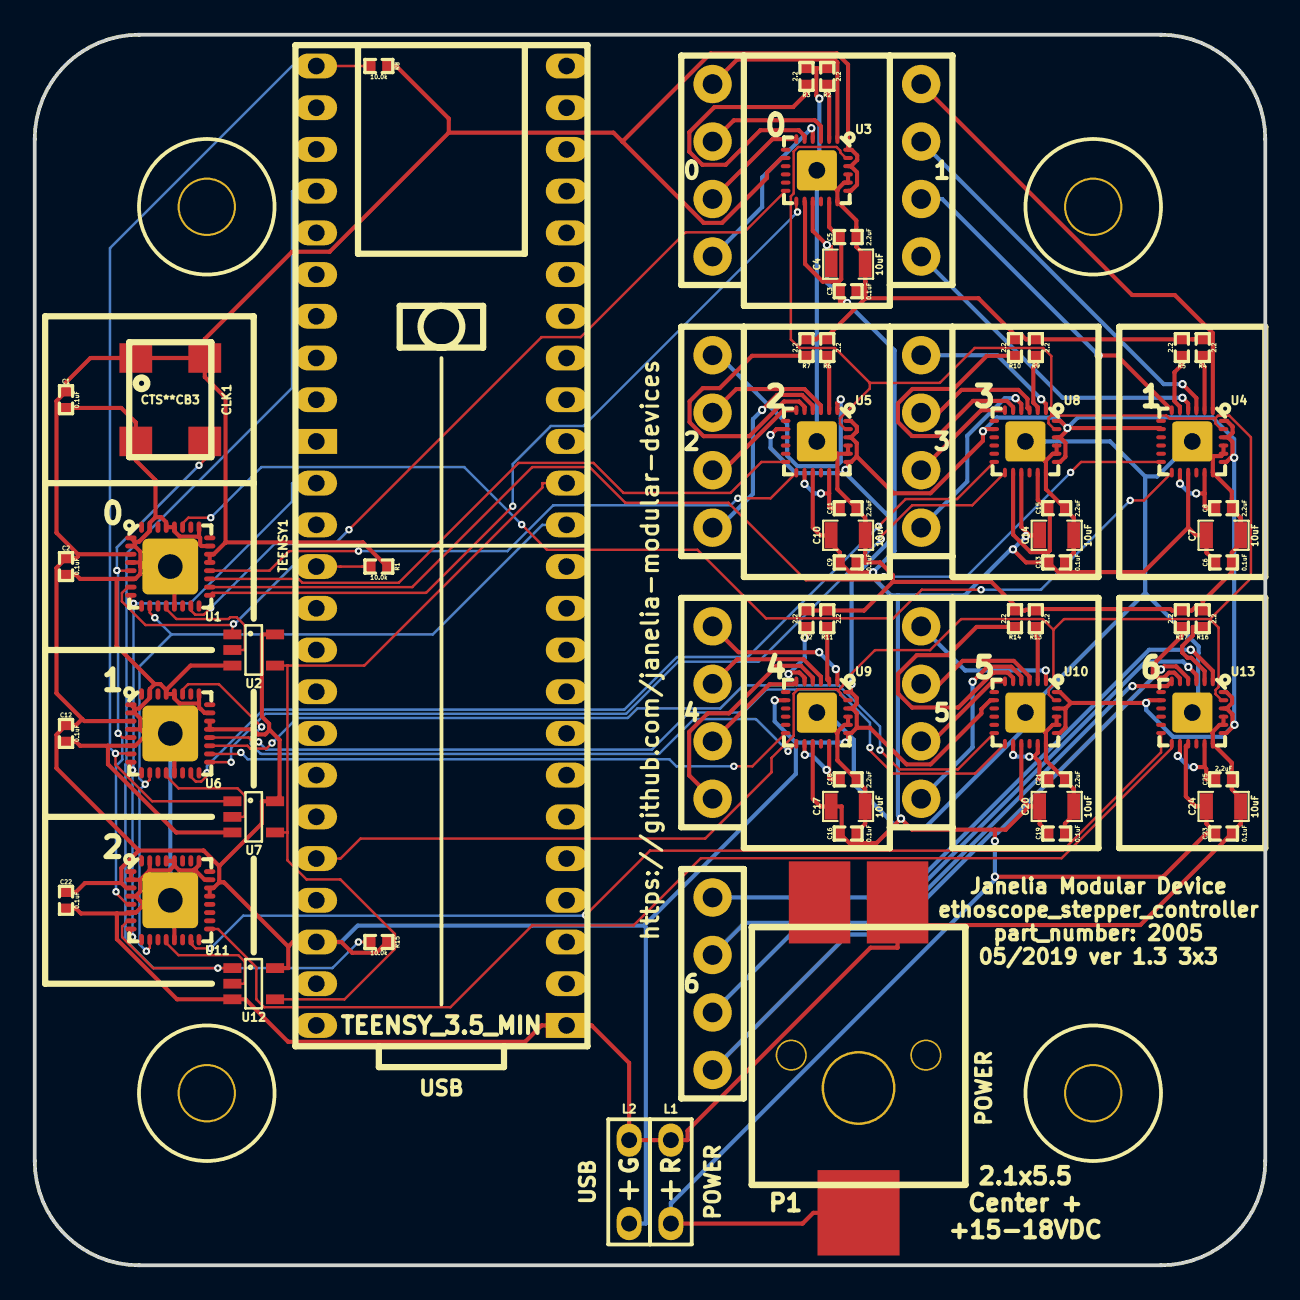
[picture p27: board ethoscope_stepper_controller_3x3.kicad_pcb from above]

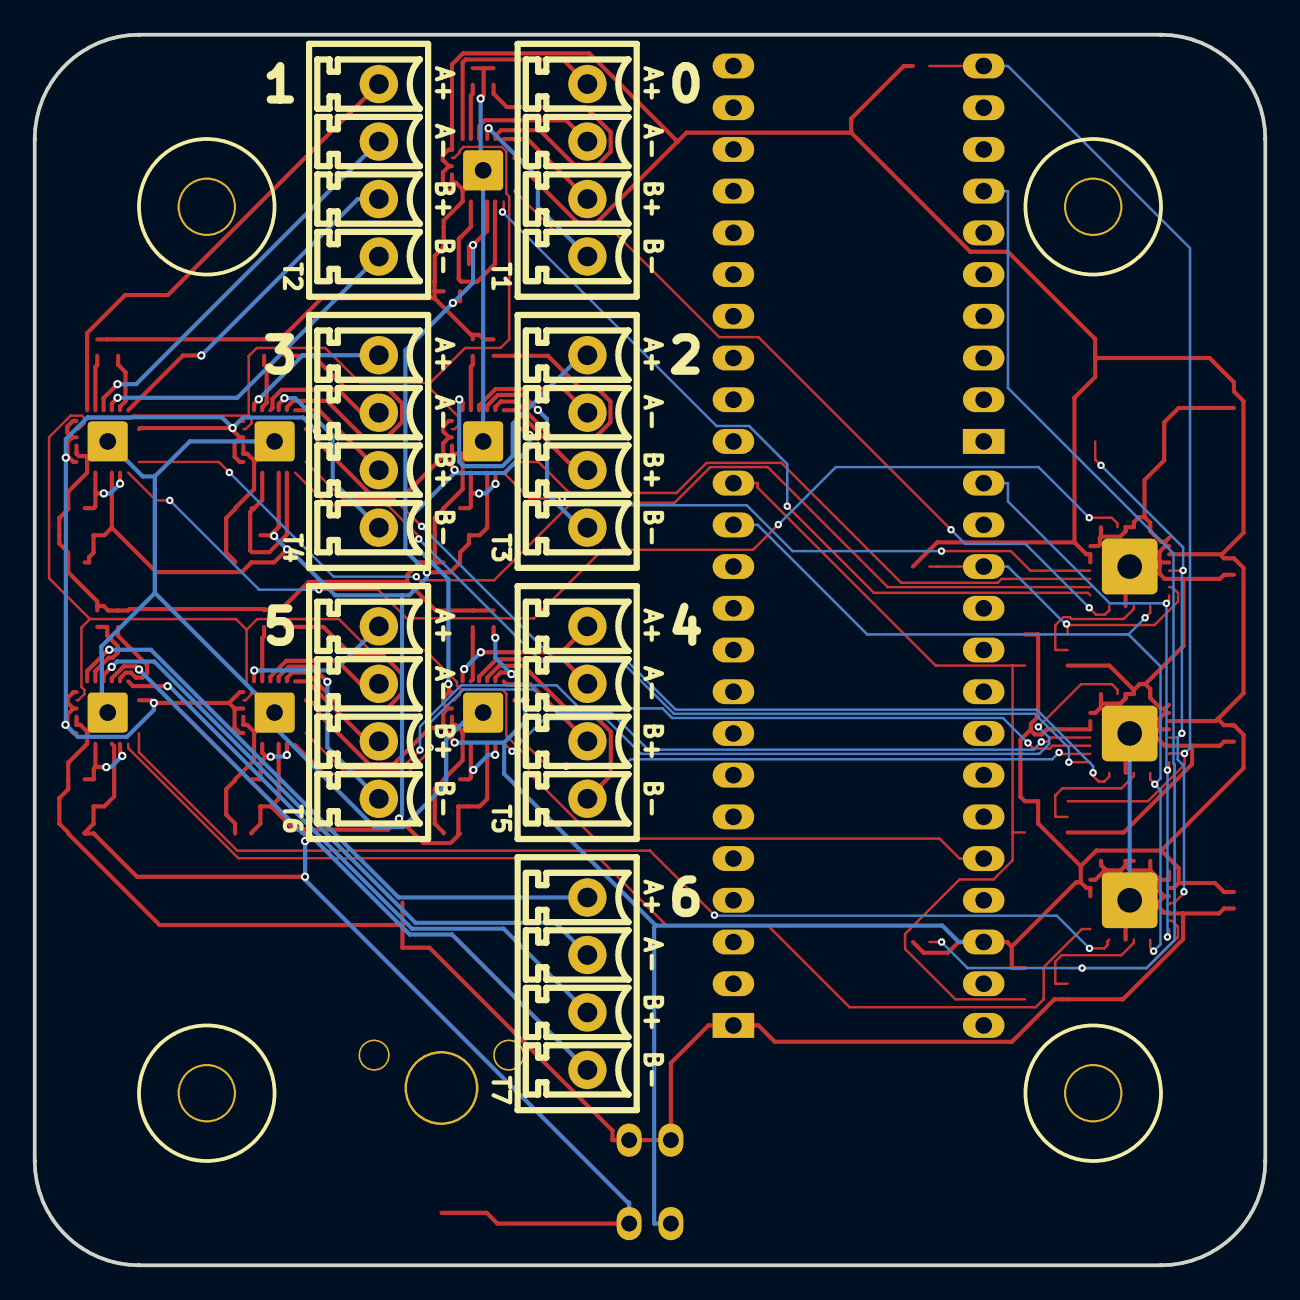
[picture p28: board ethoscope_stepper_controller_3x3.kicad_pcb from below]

Board: 2 copper layers, 74.9 x 74.9 mm, 71 parts (7 on the bottom side), 77 nets.

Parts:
C1, C2, C3, C6, C9, C12, C13, C16, C19, C22, C23: 0.1uF; SM0402
C4, C7, C10, C14, C17, C20, C24: 10uF; SM0805
C5, C8, C11, C15, C18, C21, C25: 2.2uF; SM0402
CLK1: CLK_32MHZ; CTS_SMD_4_7X5MM
L1: LED_24V_RED; LED_555-3XXX_R
L2: LED_5V_GRN; LED_555-3XXX_G
MH1, MH2, MH3, MH4: MOUNT_HOLE; MOUNTING_HOLE_4-40
P1: PWR_JACK_2.1x5.5_SMD_VERT; DCJACK_3PIN_SMD_VERT
R1, R8, R15: 10.0k; SM0402
R2, R3, R4, R5, R6, R7, R9, R10, R11, R12, R13, R14, R16, R17: 2.2; SM0402
T1, T2, T3, T4, T5, T6, T7: TERM_BLK_HDR_4POS_VERT_0.138IN
TEENSY1: TEENSY_3.5_MIN
U1, U6, U11: TMC429; QFN-5x5-32
U2, U7, U12: BUFFER_TRI_STATE; SOT-23-5
U3, U4, U5, U8, U9, U10, U13: DRV8846; VQFN-4x4-24

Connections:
+3V3: C1.1, C2.1, C12.1, C22.1, CLK1.1, CLK1.4, L2.1, R1.1, R8.1, R15.1, TEENSY1.3V3, U1.3, U1.21, U1.22, U2.5, U3.8, U3.19, U3.22, U3.24, U4.8, U4.19, U4.22, U4.24, U5.8, U5.19, U5.22, U5.24, U6.3, U6.21, U6.22, U7.5, U8.8, U8.19, U8.22, U8.24, U9.8, U9.19, U9.22, U9.24, U10.8, U10.19, U10.22, U10.24, U11.3, U11.21, U11.22, U12.5, U13.8, U13.19, U13.22, U13.24
/MISO: TEENSY1.12, U2.4, U7.4, U12.4
/MOSI: TEENSY1.11, U1.10, U6.10, U11.10
/SCK: TEENSY1.13, U1.8, U6.8, U11.8
/ethoscope_3x3/CLK: CLK1.3, U1.5, U6.5, U11.5
/ethoscope_3x3/tmc429_0/DIR_0: U1.17, U3.13
/ethoscope_3x3/tmc429_0/DIR_1: U1.27, U4.13
/ethoscope_3x3/tmc429_0/DIR_2: U1.20, U5.13
/ethoscope_3x3/tmc429_0/MISO_UB: U1.12, U2.2
/ethoscope_3x3/tmc429_0/STEP_0: U1.15, U3.12
/ethoscope_3x3/tmc429_0/STEP_1: U1.18, U4.12
/ethoscope_3x3/tmc429_0/STEP_2: U1.19, U5.12
/ethoscope_3x3/tmc429_0/stepper_driver_0/AISEN: R2.1, U3.2
/ethoscope_3x3/tmc429_0/stepper_driver_0/A_+: T1.4, U3.1
/ethoscope_3x3/tmc429_0/stepper_driver_0/A_-: T1.3, U3.3
/ethoscope_3x3/tmc429_0/stepper_driver_0/BISEN: R3.1, U3.5
/ethoscope_3x3/tmc429_0/stepper_driver_0/B_+: T1.2, U3.6
/ethoscope_3x3/tmc429_0/stepper_driver_0/B_-: T1.1, U3.4
/ethoscope_3x3/tmc429_0/stepper_driver_0/VINT: C5.1, U3.14, U3.17
/ethoscope_3x3/tmc429_0/stepper_driver_1/AISEN: R4.1, U4.2
/ethoscope_3x3/tmc429_0/stepper_driver_1/A_+: T2.4, U4.1
/ethoscope_3x3/tmc429_0/stepper_driver_1/A_-: T2.3, U4.3
/ethoscope_3x3/tmc429_0/stepper_driver_1/BISEN: R5.1, U4.5
/ethoscope_3x3/tmc429_0/stepper_driver_1/B_+: T2.2, U4.6
/ethoscope_3x3/tmc429_0/stepper_driver_1/B_-: T2.1, U4.4
/ethoscope_3x3/tmc429_0/stepper_driver_1/VINT: C8.1, U4.14, U4.17
/ethoscope_3x3/tmc429_0/stepper_driver_2/AISEN: R6.1, U5.2
/ethoscope_3x3/tmc429_0/stepper_driver_2/A_+: T3.4, U5.1
/ethoscope_3x3/tmc429_0/stepper_driver_2/A_-: T3.3, U5.3
/ethoscope_3x3/tmc429_0/stepper_driver_2/BISEN: R7.1, U5.5
/ethoscope_3x3/tmc429_0/stepper_driver_2/B_+: T3.2, U5.6
/ethoscope_3x3/tmc429_0/stepper_driver_2/B_-: T3.1, U5.4
/ethoscope_3x3/tmc429_0/stepper_driver_2/VINT: C11.1, U5.14, U5.17
/ethoscope_3x3/tmc429_1/DIR_0: U6.17, U8.13
/ethoscope_3x3/tmc429_1/DIR_1: U6.27, U9.13
/ethoscope_3x3/tmc429_1/DIR_2: U6.20, U10.13
/ethoscope_3x3/tmc429_1/MISO_UB: U6.12, U7.2
/ethoscope_3x3/tmc429_1/STEP_0: U6.15, U8.12
/ethoscope_3x3/tmc429_1/STEP_1: U6.18, U9.12
/ethoscope_3x3/tmc429_1/STEP_2: U6.19, U10.12
/ethoscope_3x3/tmc429_1/stepper_driver_0/AISEN: R9.1, U8.2
/ethoscope_3x3/tmc429_1/stepper_driver_0/A_+: T4.4, U8.1
/ethoscope_3x3/tmc429_1/stepper_driver_0/A_-: T4.3, U8.3
/ethoscope_3x3/tmc429_1/stepper_driver_0/BISEN: R10.1, U8.5
/ethoscope_3x3/tmc429_1/stepper_driver_0/B_+: T4.2, U8.6
/ethoscope_3x3/tmc429_1/stepper_driver_0/B_-: T4.1, U8.4
/ethoscope_3x3/tmc429_1/stepper_driver_0/VINT: C15.1, U8.14, U8.17
/ethoscope_3x3/tmc429_1/stepper_driver_1/AISEN: R11.1, U9.2
/ethoscope_3x3/tmc429_1/stepper_driver_1/A_+: T5.4, U9.1
/ethoscope_3x3/tmc429_1/stepper_driver_1/A_-: T5.3, U9.3
/ethoscope_3x3/tmc429_1/stepper_driver_1/BISEN: R12.1, U9.5
/ethoscope_3x3/tmc429_1/stepper_driver_1/B_+: T5.2, U9.6
/ethoscope_3x3/tmc429_1/stepper_driver_1/B_-: T5.1, U9.4
/ethoscope_3x3/tmc429_1/stepper_driver_1/VINT: C18.1, U9.14, U9.17
/ethoscope_3x3/tmc429_1/stepper_driver_2/AISEN: R13.1, U10.2
/ethoscope_3x3/tmc429_1/stepper_driver_2/A_+: T6.4, U10.1
/ethoscope_3x3/tmc429_1/stepper_driver_2/A_-: T6.3, U10.3
/ethoscope_3x3/tmc429_1/stepper_driver_2/BISEN: R14.1, U10.5
/ethoscope_3x3/tmc429_1/stepper_driver_2/B_+: T6.2, U10.6
/ethoscope_3x3/tmc429_1/stepper_driver_2/B_-: T6.1, U10.4
/ethoscope_3x3/tmc429_1/stepper_driver_2/VINT: C21.1, U10.14, U10.17
/ethoscope_3x3/tmc_429_2/DIR_0: U11.17, U13.13
/ethoscope_3x3/tmc_429_2/MISO_UB: U11.12, U12.2
/ethoscope_3x3/tmc_429_2/STEP_0: U11.15, U13.12
/ethoscope_3x3/tmc_429_2/stepper_driver_0/AISEN: R16.1, U13.2
/ethoscope_3x3/tmc_429_2/stepper_driver_0/A_+: T7.4, U13.1
/ethoscope_3x3/tmc_429_2/stepper_driver_0/A_-: T7.3, U13.3
/ethoscope_3x3/tmc_429_2/stepper_driver_0/BISEN: R17.1, U13.5
/ethoscope_3x3/tmc_429_2/stepper_driver_0/B_+: T7.2, U13.6
/ethoscope_3x3/tmc_429_2/stepper_driver_0/B_-: T7.1, U13.4
/ethoscope_3x3/tmc_429_2/stepper_driver_0/VINT: C25.1, U13.14, U13.17
/~CS_429_0: R1.2, TEENSY1.15, U1.7, U2.1
/~CS_429_1: R8.2, TEENSY1.33, U6.7, U7.1
/~CS_429_2: R15.2, TEENSY1.36, U11.7, U12.1
/~SLEEP: TEENSY1.22, U3.23, U4.23, U5.23, U8.23, U9.23, U10.23, U13.23
GND: C1.2, C2.2, C3.2, C4.2, C5.2, C6.2, C7.2, C8.2, C9.2, C10.2, C11.2, C12.2, C13.2, C14.2, C15.2, C16.2, C17.2, C18.2, C19.2, C20.2, C21.2, C22.2, C23.2, C24.2, C25.2, CLK1.2, L1.2, L2.2, P1.2, R2.2, R3.2, R4.2, R5.2, R6.2, R7.2, R9.2, R10.2, R11.2, R12.2, R13.2, R14.2, R16.2, R17.2, TEENSY1.GND, U1.1, U1.2, U1.4, U1.6, U1.13, U1.23, U1.25, U1.28, U1.29, U1.31, U1.PAD, U2.3, U3.18, U3.20, U3.21, U3.PAD, U4.18, U4.20, U4.21, U4.PAD, U5.18, U5.20, U5.21, U5.PAD, U6.1, U6.2, U6.4, U6.6, U6.13, U6.23, U6.25, U6.28, U6.29, U6.31, U6.PAD, U7.3, U8.18, U8.20, U8.21, U8.PAD, U9.18, U9.20, U9.21, U9.PAD, U10.18, U10.20, U10.21, U10.PAD, U11.1, U11.2, U11.4, U11.6, U11.13, U11.23, U11.25, U11.28, U11.29, U11.31, U11.PAD, U12.3, U13.18, U13.20, U13.21, U13.PAD
VAA: C3.1, C4.1, C6.1, C7.1, C9.1, C10.1, C13.1, C14.1, C16.1, C17.1, C19.1, C20.1, C23.1, C24.1, L1.1, P1.1, U3.15, U4.15, U5.15, U8.15, U9.15, U10.15, U13.15

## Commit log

2018-08-12 Initial commit.
    [ethoscope_stepper_controller.kicad_pcb, ethoscope_stepper_controller.sch]
2018-08-12 Added files from step_dir_controller.
    [ethoscope_stepper_controller.kicad_pcb, ethoscope_stepper_controller.sch, step_dir.sch, tmc429.sch]
2018-08-13 Added teensy to schematic.
    [ethoscope_stepper_controller.sch, step_dir.sch, tmc429.sch]
2018-08-13 Added power jack.
    [ethoscope_stepper_controller.sch, step_dir.sch, supplemental_digikey_parts.csv]
2018-08-14 Added sense resistors.
    [ethoscope_stepper_controller.sch, step_dir.sch, tmc429.sch]
2018-08-14 Renamed schematics.
    [stepper_driver.sch, tmc429_1_motor.sch]
2018-08-14 Finished schematics.
    [ethoscope_stepper_controller.sch, stepper_driver.sch, tmc429.sch, tmc429_1_motor.sch]
2018-08-14 Annotated schematics.
    [ethoscope_stepper_controller.sch, stepper_driver.sch, tmc429.sch, tmc429_1_motor.sch]
2018-08-14 Fixed footprints.
    [ethoscope_stepper_controller.kicad_pcb, ethoscope_stepper_controller.sch, stepper_driver.sch, tmc429.sch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]
2018-08-14 Initial layout.
    [ethoscope_stepper_controller.kicad_pcb]
2018-08-15 Switched to 0805 parts.
    [ethoscope_stepper_controller.kicad_pcb, ethoscope_stepper_controller.sch, stepper_driver.sch, tmc429.sch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]
2018-08-15 Added a pull-up resistor and tri-state buffer.
    [ethoscope_stepper_controller.kicad_pcb, stepper_driver.sch, tmc429.sch]
2018-08-15 Placed more parts, but saved with errors.
    [ethoscope_stepper_controller.kicad_pcb, ethoscope_stepper_controller.sch, stepper_driver.sch, tmc429.sch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]
2018-08-21 Initial part placement.
    [ethoscope_stepper_controller.dsn, ethoscope_stepper_controller.kicad_pcb, ethoscope_stepper_controller.sch, stepper_driver.sch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]
2018-08-21 Use 0402 parts when possible.
    [ethoscope_stepper_controller.dsn, ethoscope_stepper_controller.kicad_pcb, ethoscope_stepper_controller.sch, stepper_driver.sch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]
2018-08-22 Added autorouted tracks.
    [ethoscope_stepper_controller.kicad_pcb]
2018-08-22 Moved traces to pass bug check.
    [ethoscope_stepper_controller.kicad_pcb]
2018-08-22 ethoscope_stepper_controller -> ethoscope_stepper_controller_3x3.
    [ethoscope_stepper_controller_3x3.dsn, ethoscope_stepper_controller_3x3.kicad_pcb, ethoscope_stepper_controller_3x3.sch, stepper_driver.sch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]
2018-08-22 Finished version 1.0.
    [ethoscope_stepper_controller_3x3-B.Cu.gbl, ethoscope_stepper_controller_3x3-B.Mask.gbs, ethoscope_stepper_controller_3x3-B.SilkS.gbo, ethoscope_stepper_control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]
2018-08-22 Generated documentation.
    [digikey_parts.csv, supplemental_digikey_parts.csv]
2018-08-23 Added digikey_order.
    [digikey_order.csv]
2018-09-11 Fixed error in supplemental bom.
    [supplemental_digikey_parts.csv]
2018-09-14 Added motors to bom.
    [supplemental_digikey_parts.csv]
2018-09-18 Rearranged schematics.
    [ethoscope_3x3.sch, ethoscope_stepper_controller_3x3.kicad_pcb, ethoscope_stepper_controller_3x3.sch, stepper_driver.sch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]
2018-09-18 Ready for autorouting.
    [ethoscope_3x3.sch, ethoscope_stepper_controller_3x3.dsn, ethoscope_stepper_controller_3x3.kicad_pcb, ethoscope_stepper_controller_3x3.sch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]
2018-09-19 Finished autorouting.
    [ethoscope_stepper_controller_3x3.kicad_pcb]
2018-09-19 Updated documentation.
    [digikey_parts.csv]
2019-01-04 Switch current sense resistor from 5.1 to 3.3
    [ethoscope_3x3.sch, ethoscope_stepper_controller_3x3.sch, stepper_driver.sch, tmc429.sch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]
2019-02-05 Progress towards v1.2
    [ethoscope_3x3.sch, ethoscope_stepper_controller_3x3-B.Cu.gbl, ethoscope_stepper_controller_3x3-B.Mask.gbs, ethoscope_stepper_controller_3x3-B_Cu.gbl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]
2019-02-06 Update documentation
    [digikey_order.csv, digikey_parts.csv, ethoscope_stepper_controller_3x3.kicad_pcb]
2019-04-22 Progress towards v1.3
    [ethoscope_3x3.sch, ethoscope_stepper_controller_3x3.dsn, ethoscope_stepper_controller_3x3.kicad_pcb, ethoscope_stepper_controller_3x3.sch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]
2019-05-06 Update date
    [ethoscope_stepper_controller_3x3.kicad_pcb]
2021-09-21 Remove ignored files
    [ethoscope_stepper_controller_3x3.dsn]
